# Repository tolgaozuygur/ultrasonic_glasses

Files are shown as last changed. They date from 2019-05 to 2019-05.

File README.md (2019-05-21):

# Ultrasonic Glasses for Visually Impaired
This is an electronic glasses extension that turns distance data into sound to help visually impaired navigate. Initially built it on my YouTube channel <a href="https://www.youtube.com/channel/UCMPCc9hZ-YBZkEon9tzESVA" target="_blank">Hallederiz</a>, it is the first prototype of an easy to build device to help visually impaired. 

Since this is a proof of content it is bulky and requires to be mounted on a pair of safety glasses.

We have tested this version with the Association of Blinds of Turkey and received lots of positive feedback with many ideas to upgrade the device further.

On the next version I intend to shrink it's size down and make it attachable to any existing pair of glasses / sun glasses. 

> Here is how it looks when assembled

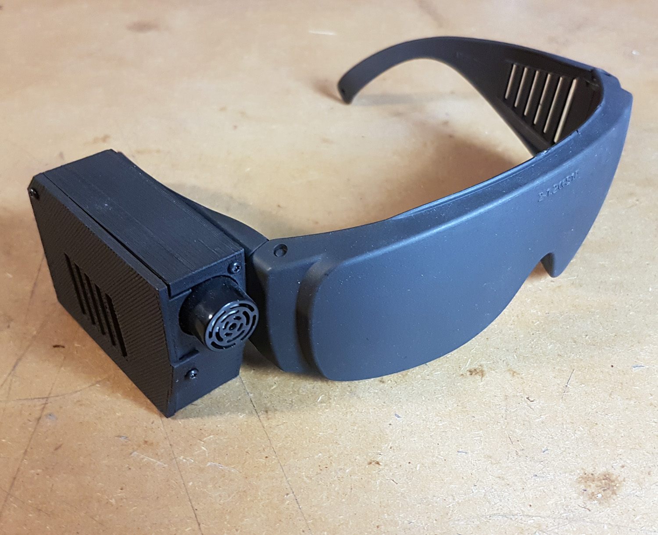
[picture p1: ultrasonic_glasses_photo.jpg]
Ultrasonic Glasses


## Build it!
Building the device is quite simple -that's the objective-. You need to 3d print a couple of simple parts, and need some very basic soldering skills to build the circuit. Then upload the arduino code and it will work right away.

The building process is documented on the YouTube channel <a href="https://www.youtube.com/channel/UCMPCc9hZ-YBZkEon9tzESVA" target="_blank">Hallederiz</a>, the channel is in Turkish, but even though it's in Turkish you can still watch the progress and get some ideas about how to assemble the device properly. I intend to add English subtitles soon.

## Parts Required
- <a href="https://www.adafruit.com/product/982" target="_blank">1x Maxbotix Ultrasonic Rangefinder - LV-EZ4</a>
- <a href="https://store.arduino.cc/usa/arduino-nano" target="_blank">1x Arduino Nano</a>
- <a href="https://www.seeedstudio.com/Lipo-Rider-v1-3-p-2403.html" target="_blank">1x Lipo Rider 1.3</a>
- <a href="https://www.e-switch.com/product-catalog/rocker/product-lines/ra8-series-power-rocker-switch#.XOM_lcgzaUk" target="_blank">Rocker Switch</a>
- <a href="https://www.adafruit.com/product/258" target="_blank">LiPo Battery</a>
- 2mm screws
- Jumper Cables 
- Heat Shrinking Tube
- A pair of generic safety glasses

> You can use an Arduino Mini Pro to save space. You can also use a clone if you're tight on budget.
> Any LiPo battery would work, just check the dimensions of the 3d case to be sure it will fit.
> You can use a small LiPo Charger and a small DC-DC step-up board instead of the Lipo Rider to save even more space.

## Soldering the circuit
Solder the components together based on the diagram below. It is quite simple, just free-form it using jumper cables and heat shrinking tubes. Be sure there is no short circuit when placing the circuit in the box, use insulation tape on the boards if required.

> I couldn't find the LiPo rider in Fritzing, so I substituted it with a SparkFun LiPo charger in the diagram.
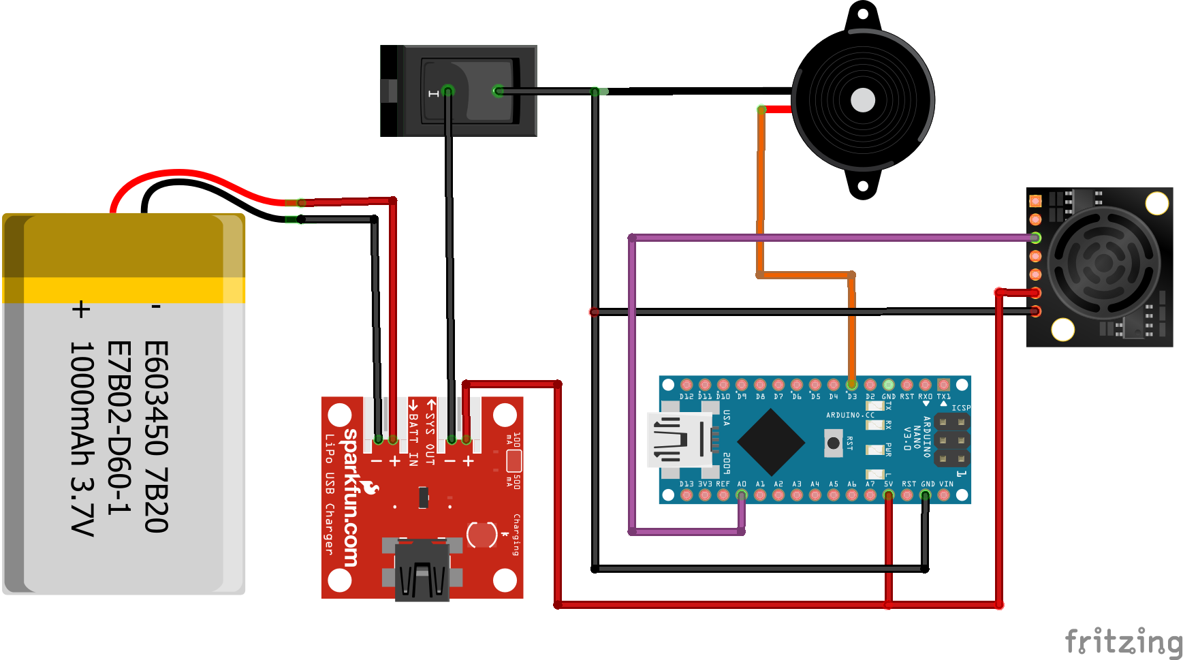
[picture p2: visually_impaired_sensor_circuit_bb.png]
Ultrasonic Sensor Circuit Diagram


## 3d Printing and Assembling the Case
Print the stl files in the 3d_files folder. The do not need any support, just print them as they are. (make sure you lay them flat in your slicer). The ultrasonic_glasses_case_spacer.stl file was required to straighten the case on the safety glasses we used (glued it between the case and the glasses), you might not need it. 

Try to align the charging port of the LiPo Rider with the hole on the case. 

You can also paint the case and the glasses to make it look a little bit more polished. I used the color Tar Black from Molotov. 

>Here is a photo of the assembled device. The battery is behind the LiPo Rider.

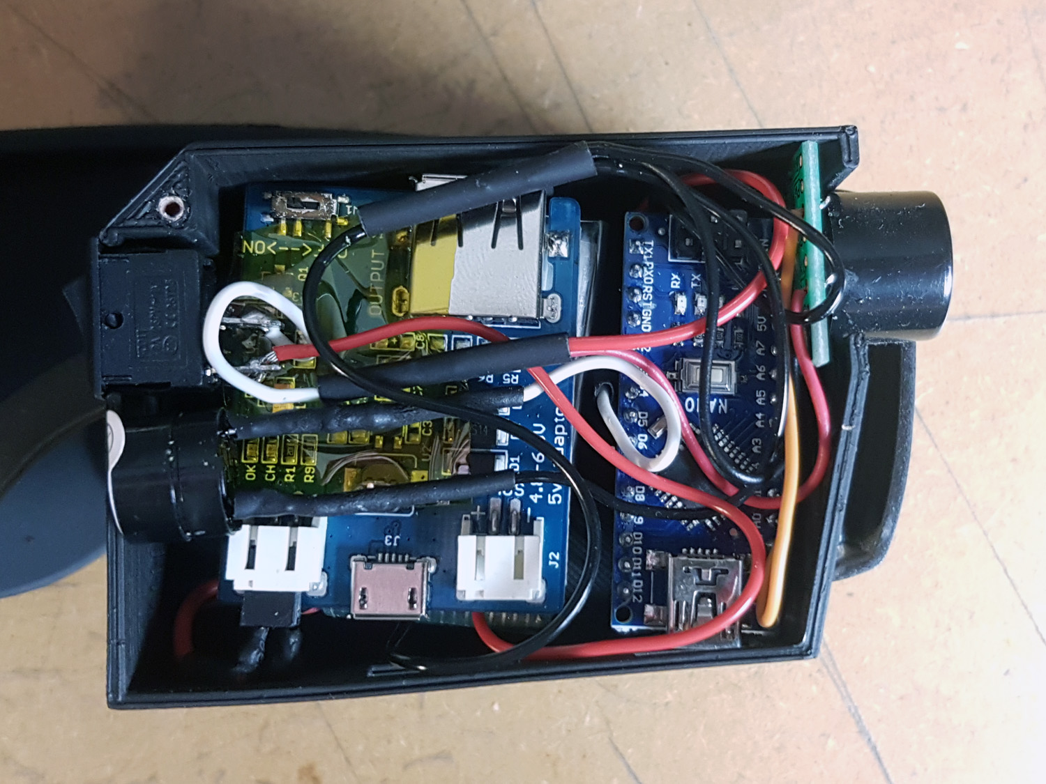
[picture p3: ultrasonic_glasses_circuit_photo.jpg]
Ultrasonic Sensor Circuit


## Finalizing the Device
Just upload the ultrasonic_glasses.ino to the Arduino, close the case, charge the battery and turn it on. For the first few seconds the device will make a constant beeping sound to let the ultrasonic sensor do first calibration. After that it will start beeping based on the distance of the objects you are looking. 

## Final words
As said, this is a proof of concept. Feel free to fork it to upgrade / simplify it even further. Also I'd be super happy if you send me an email (tolgaozuygur at gmail) if you build one and test it with a visually impaired friend of yours. After all, the purpose of this project is to help people to live a more comfortable life through a proper use of technology. It would be very humbling and joyful to see it in use.

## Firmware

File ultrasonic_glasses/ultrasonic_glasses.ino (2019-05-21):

/*
 Ultrasonic Glasses Project for Visually Impaired
 by Tolga Ozuygur and Cem Sina Cetin
*/

const int anPin = 0;
long mm;
int buzzerPin = 3;
long buzzerBeepDuration = 40;
long buzzerBeepMillis = 0;
long buzzerFrequencyDuration = 0;
long buzzerPreviousBeepMillis = 0;
float mmToBuzzerFrequencyMultiplier = 0.6;

void setup(){
  Serial.begin(9600);
  pinMode(buzzerPin, OUTPUT);
  calibrationWarning(3000, 500, 100);
}

void loop(){
  mm = analogRead(anPin) * 5;
  buzzerFrequencyDuration = mm * mmToBuzzerFrequencyMultiplier;
  if(buzzerPreviousBeepMillis + buzzerFrequencyDuration < millis()){
    buzzerPreviousBeepMillis =  millis();
    buzzerBeepMillis = millis() + buzzerBeepDuration;
    digitalWrite(buzzerPin, HIGH);
  }
  if(buzzerBeepMillis < millis()){
    digitalWrite(buzzerPin, LOW);
  }
  Serial.println(buzzerFrequencyDuration);
  delay(5);
}

void calibrationWarning(int totalDur, int beepDur, int silenceDur){
  int oneBeep = beepDur + silenceDur;
  for(int i = 0; i < totalDur; i+=oneBeep) {
    digitalWrite(buzzerPin, HIGH);
    delay(beepDur);
    digitalWrite(buzzerPin, LOW);
    delay(silenceDur);
  }
}
